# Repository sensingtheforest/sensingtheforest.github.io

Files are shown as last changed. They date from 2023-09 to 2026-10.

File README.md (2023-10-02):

# Sensing the Forest - project website

This project website is using [11TA](https://github.com/11ta/11ta-template/) - 11ty, TailwindCSS, & Alpine.js Template.

## Run it manually in localhost

- Clone the repository locally
- Run `npm install` to install dependencies
- `npm run dev` to work locally

## Run it in production

- `npm run build` to work in production

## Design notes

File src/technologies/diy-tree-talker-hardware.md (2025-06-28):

---
title: DIY Tree Talker | Hardware
date: 2025-06-27T07:30:00.000Z
excerpt: The hardware component of the DIY Tree Talker.
layout: post
draft:
seo:
  title: DIY Tree Talker | Hardware
  description: The hardware component of the DIY Tree Talker.
  image: technologies/diy-tree-talker-hardware-northern-research-station.jpg
images: # relative to /src/assets/images/
  #feature: exhibition/Peter-Batchelor-Dendrophone-overview_by_Shuoyang_Zheng.jpg
  thumb: technologies/diy-tree-talker-hardware-northern-research-station.jpg
  align: # object-center (default) - other options at https://tailwindcss.com/docs/object-position
  height: h-auto # optional. Default = h-48 md:h-1/3
hero: graphic # options: carousel, graphic, video, split (text & image)
heroSettings:
  height:
    mobile: h-1/1 # options = h-1/1 (default = full screen), h-1/2, h-1/3, h-3/4, h-9/10, h-48 (12rem, 192px), h-56 (14rem, 224px), h-64 (16rem, 256px)
    desktop: # leave blank to inherit "mobile" height (default = full screen)
  bg:
    color: bg-green-900 # default bg-black
    image: technologies/diy-tree-talker-hardware-northern-research-station.jpg # relative to /assets/images/
    imagePosition: # options = bg-center (default), bg-left, bg-right
    video: # pixabay-john-macdougall.mp4 # local relative /assets/video/, or full https://... if remote?
    opacityMobile: opacity-50 # options opacity-n, 5, 10, 15, 20, 25, 50, 75, 100 (default)
    opacityDesktop: opacity-75 # Leave blank to inherit opacityMobile, use same options as opacityMobile
  headingText: DIY Tree Talker | Hardware
  headingTextColor: # default = text-white (can use any TailwindCSS text-[color]-[xxx])
  headingTextCase: # default = as typed - options: uppercase, lowercase, capitalize
  subheadingText: #
    #Let the Forest Speak using the Internet of Things, Acoustic Ecology and Creative AI<br /><span style="color:grey">AHRC-funded project (2023-25) : AH/X011585/1</span>
  subheadingTextColor: # Leave empty to inherit headingTextColor or default (text-white) or use any text-[color]-[xxx]
  buttonText: # Contact Us... # no button generated if left blank
  buttonURL: # /contact/ # full url required. Example: https://thisdomain.com/somepage/
  buttonTextColor: # leave blank to inherit from /src/_data/colors.buttonCustom or buttonDefault
  buttonBgColor: # leave blank to inherit from /src/_data/colors.buttonCustom.bg or buttonDefault.bg
  buttonBgHover: # leave blank to inherit from /src/_data/colors.buttonCustom.bgHover or buttonDefault.bgHover
  buttonBorder: # leave blank to inherit from /src/_data/colors.buttonCustom.border or buttonDefault.border
  
tags:
  - technologies

---

### Authors: Mahmoud B. Elmokadem, Krishna Nama Manjunatha, Georgios Xenakis, Anna Xambó

*A Real-World Deployment of the Streaming Unit. 
:camera: *Photo by Mahmoud B. Elmokadem.**

The system integrates a suite of sensors—including a capacitive soil moisture sensor, a combined temperature and humidity sensor, and a bespoke dendrometer, connected to a Raspberry Pi Zero 2W for data acquisition and processing.

A custom tree-talker prototype is being developed, using a participatory design approach. The device comprises a soil moisture sensor, a combined temperature and humidity sensor, and a bespoke dendrometer, connected to a Raspberry Pi Zero 2W single-board computer for data acquisition. You can read about our dendrometer in our tutorial [Design of Cost Effective IOT Dendrometer Sensor for Environmental Monitoring](/2025/05/05/design-of-cost-effective-iot-dendrometer-sensor-for-environmental-monitoring/).

<div class="flex justify-center items-center">
<figure>
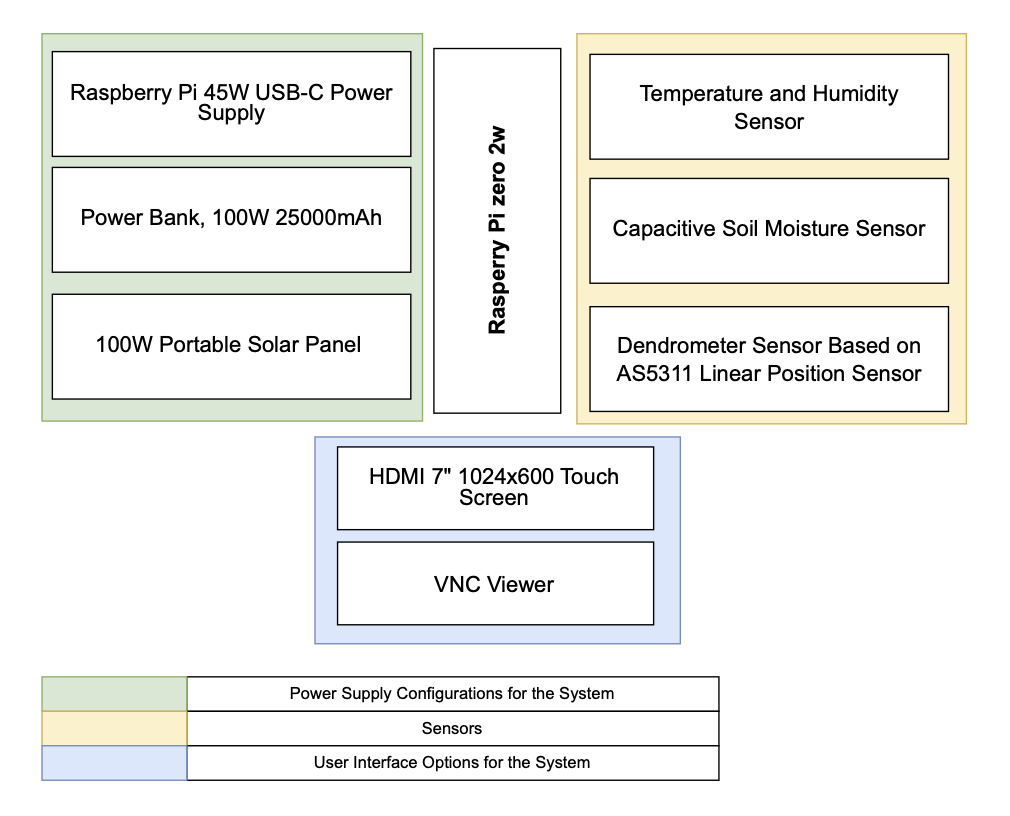
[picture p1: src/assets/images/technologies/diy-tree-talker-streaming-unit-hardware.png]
Hardware Configuration Overview of the Sensing Unit.

<figcaption>Hardware Configuration Overview of the Sensing Unit.</figcaption>
</figure>
</div>

Traditional dendrometer systems often come with high costs and complex installation requirements, limiting their accessibility for small-scale researchers; thus, a custom, cost-effective dendrometer was iteratively designed, based on Clonch and colleagues’ open-source magnetic carbon fibre dendrometer [1]. To further reduce costs, we replaced the carbon fibre frame with 3D-printed components made from high-density PLA, and captured data using the Raspberry Pi, reducing the overall cost by 50%, without compromising core functionality.
 
The main chassis of the dendrometer sensor is secured to the tree/plant using a strap, ensuring stable attachment without causing any damage to the bark or applying external stress. A movable component, referred to as the T-shaped magnet mount, is connected to the chassis via an extension spring and is positioned to slide forward and backwards in response to the tree/stem’s natural expansion or contraction. These micro-movements—often in the micrometer range—are detected by the AS5311 magnetic linear encoder, which precisely tracks the relative position of the magnet. The sensor transmits data to the Raspberry Pi Zero 2W via a PWM (Pulse Width Modulation) signal, which is then processed and converted into readable measurements that reflect changes in stem diameter over time. The sensor is integrated into a larger sensing unit that also includes additional climatic sensors to monitor environmental parameters such as temperature, humidity, and soil moisture, alongside the tree’s natural expansion or contraction. All collected data is streamed to a central server for real-time monitoring and analysis.

<div class="flex justify-center items-center">
<figure>
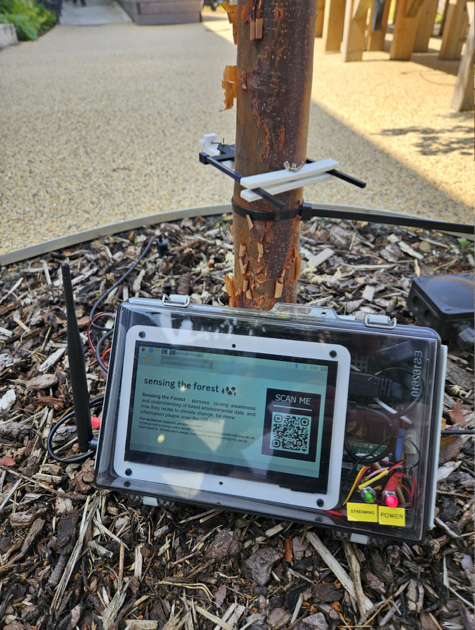
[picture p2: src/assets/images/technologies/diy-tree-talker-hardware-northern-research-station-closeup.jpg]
Closeup of a real-world deployment of the streaming unit.

<figcaption>Closeup of a real-world deployment of the streaming unit. Photo by Mahmoud B. Elmokadem.</figcaption>
</figure>
</div>

:fire: We are currently running a participatory design user study. We will share the hardware code soon on our [GitHub project webpage](https://github.com/orgs/sensingtheforest/repositories).

## List of References

[1] Clonch, C., Huynh, M., Goto, B., Levin, A., Selker, J. and Udell, C., 2021. [High precision zero-friction magnetic dendrometer](https://www.sciencedirect.com/science/article/pii/S246806722100078X). HardwareX, 10, p.e00248.

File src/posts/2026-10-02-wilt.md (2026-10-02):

---
title: WILT – Using Solar-Powered Kinetic Art to Communicate Climate Change
date: 2026-10-01T10:00:00.000Z
excerpt: WILT is a solar-powered kinetic art installation in which five servo-driven paper flowers breathe freely or struggle depending on live air quality data fetched in real time from cities around the world. 
author: dharma-rumpal
draft:
seo:
  title:
  description:
  image: 2026/10/WILT_Dharma_Rumpal.jpg
images: # relative to /src/assets/images/
  feature: 2026/10/WILT_Dharma_Rumpal.jpg
  thumb: 2026/10/WILT_Dharma_Rumpal.jpg
  align: # object-center (default) - other options at https://tailwindcss.com/docs/object-position
  height: h-auto # optional. Default = h-48 md:h-1/3
tags:
  - climate-change
  - hardware
  - kinetic-art
  - software
  - solar
  - solar-powered  
  - theses

---

<br />

## Introduction

Climate change is one of the most pressing issues of our time, yet public engagement remains critically inadequate. Traditional communication methods such as: statistics, scientific reports, and news headlines, frequently fail to create the emotional resonance needed to inspire action. For my final year project at Queen Mary University of London, I set out to explore whether interactive art powered by renewable energy could bridge this gap in a way that data alone never could.

The result was Wilt: a solar-powered kinetic art installation in which five servo-driven paper flowers breathe freely or struggle depending on live air quality data fetched in real time from cities around the world. The piece cycles through ten globally selected cities every 45 seconds, from Reykjavik in Iceland, one of the cleanest cities on earth, to Delhi and Beijing at the other extreme. As the data changes, so does the movement of the flowers. Good air quality produces full, open blooms moving freely. Poor air quality produces slow, laboured, restricted movement. 

<div class="flex justify-center items-center">
<figure>
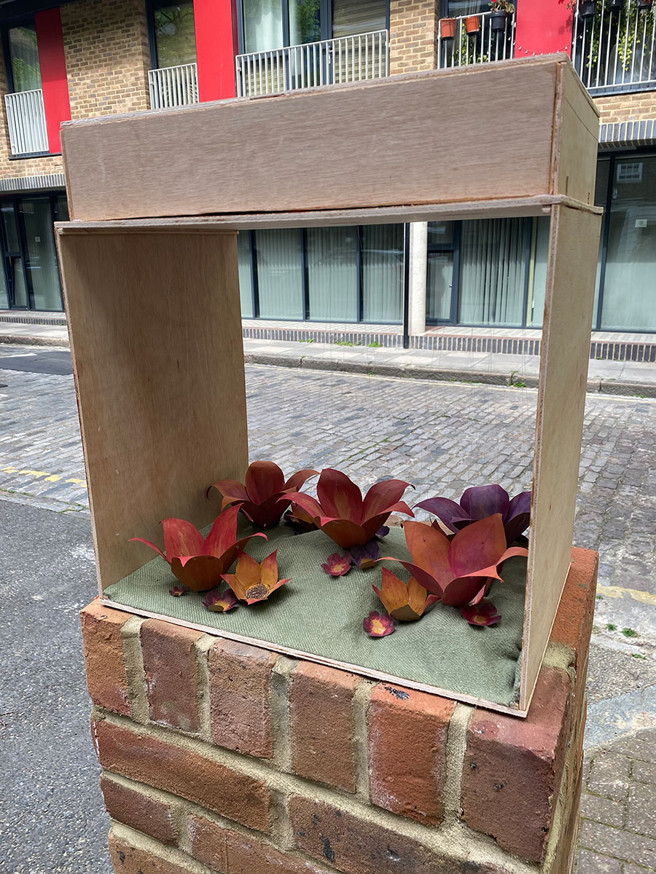
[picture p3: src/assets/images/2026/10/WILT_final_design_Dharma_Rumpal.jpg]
Final design.

<figcaption>Final design.</figcaption>
</figure>
</div>

## Development 

The technical system behind the installation brings together several layers of software and hardware working as one. An Arduino Uno microcontroller manages five SG90 servo motors through a synchronised breathing function, with movement speed and range calibrated precisely to each air quality state. A Python control script handles all the intelligence, making live API calls to the [OpenWeatherMap Air Pollution API](https://openweathermap.org/api/air-pollution), converting the data, and transmitting commands to the Arduino over USB serial. The whole system runs on renewable energy: a 5W solar panel charges an 18650 lithium-ion battery through a TP4056 charging module, stepped up to stable 5V by an XL6009 boost converter. The solar infrastructure was deliberately left visible as the power system is part of the message, not infrastructure to be hidden.

<div class="flex justify-center items-center">
<figure>
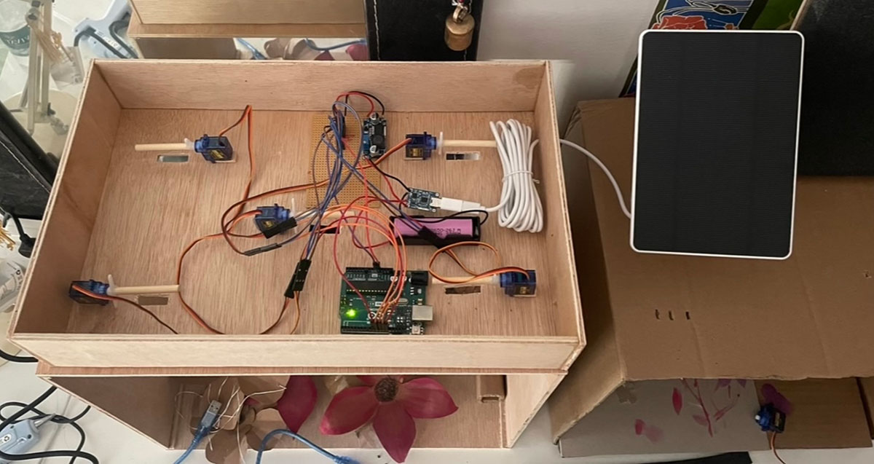
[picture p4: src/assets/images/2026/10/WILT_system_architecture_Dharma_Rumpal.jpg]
System architecture.

<figcaption>System architecture.</figcaption>
</figure>
</div>

A companion website extended the installation's reach beyond the physical display, featuring a live city monitor kept in sync with the flowers, an interactive global air quality map, and educational pages on AQI and solar power.

## Evaluation 

What distinguishes Wilt from much of the climate art that preceded it is that it was systematically evaluated. The installation was exhibited at Queen Mary University of London, where participants completed paired pre and post surveys and took part in semi-structured interviews. The findings were significant. Climate concern rose from 3.84 to 4.48 out of 5. Motivation to act increased from 3.56 to 4.35. Most strikingly, the proportion of participants who considered interactive art installations an effective method of climate communication rose from 20% before the exhibition to 96% after it. The dominant emotional responses were curiosity, hope, and inspiration, not fear or helplessness.

## Conclusion 

Wilt contributes something that has been largely absent from the field of climate communication: connection. And now a  methodological template now exists for how data-responsive kinetic art, renewable energy infrastructure, and rigorous evaluation can work together. One that future artists, researchers, and climate communicators can take, replicate, and build upon. 

## Acknowledgements

I would like to express my sincere gratitude to my supervisor Dr Anna Xambó Sedó, for her unwavering guidance, support, and feedback throughout this project. I would also like to thank Kok Ho Huen, the electronics lab manager at Queen Mary University of London, and David Wilkinson, the electronic lab technician, for their helpful knowledge and advice, and for providing access to the resources that made the physical build possible. Finally, I would like to thank my brother, Cosmo Rumpal, for composing the original music tracks that brought the installation to life. His contribution added a dominion to the project I could not have achieved alone.

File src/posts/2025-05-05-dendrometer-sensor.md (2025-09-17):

---
title: Design of Cost Effective IOT Dendrometer Sensor for Environmental Monitoring 
date: 2025-05-05T10:00:00.000Z
excerpt: In this tutorial, we introduce the design of a customised dendrometer sensor for our DIY tree talker.
author: mahmoud-elmokadem
author2: krishna-nama-manjunatha
draft: 
seo:
  title:
  description:
  image: 2025/05/DIY-tree-talker.jpg
images: # relative to /src/assets/images/
  feature: 2025/05/DIY-tree-talker.jpg
  thumb: 2025/05/DIY-tree-talker.jpg
  align: # object-center (default) - other options at https://tailwindcss.com/docs/object-position
  height: h-auto # optional. Default = h-48 md:h-1/3
tags:
  - dendrometer
  - development
  - diy-tree-talker
  - do-it-yourself
  - raspberry-pi
  - tutorials
 
---

## Introduction

Monitoring tree growth is essential for understanding forest health, ecosystem dynamics, and climate change impacts. At the heart of this process is the dendrometer sensor—an instrument designed to measure changes in a tree’s diameter over time. This helps to understand seasonal, and annual growth patterns in response to environmental conditions. As this is linked to and can be correlated with the tree diameter fluctuations with temperature, rainfall, humidity, and soil moisture and identify the stress events like droughts, heatwaves, or cold spells. Growth data of the tree can be used to estimate biomass accumulation, indicate root damage or poor soil conditions, and growth with respect to fertilizers, irrigation regimes and climate.  However, traditional dendrometer systems often come with high costs and complex installation requirements, limiting their accessibility for small-scale researchers, farmers, and institutions in low-resource settings. As environmental monitoring becomes more critical globally, there's a growing demand for affordable, reliable, and scalable solutions. A cost-effective dendrometer sensor can democratise access to valuable data, enabling broader participation in ecological research and resource management. By reducing financial barriers, we not only make long-term monitoring feasible but also support sustainable practices in both forestry and agriculture.

## Overview of Different Types of Dendrometer Sensors

There are various types of dendrometers currently used by researchers and scientists to measure changes in the diameter of trees, plants, or even fruits. While the designs may differ, they all share a similar sensing mechanism aimed at achieving the same objective: tracking dimensional changes over time to study growth patterns, water transport, and environmental stress responses. The most common types include point dendrometers, band dendrometers, and manual dendrometers as shown in Figure 1. 

<div class="flex justify-center items-center">
<figure>
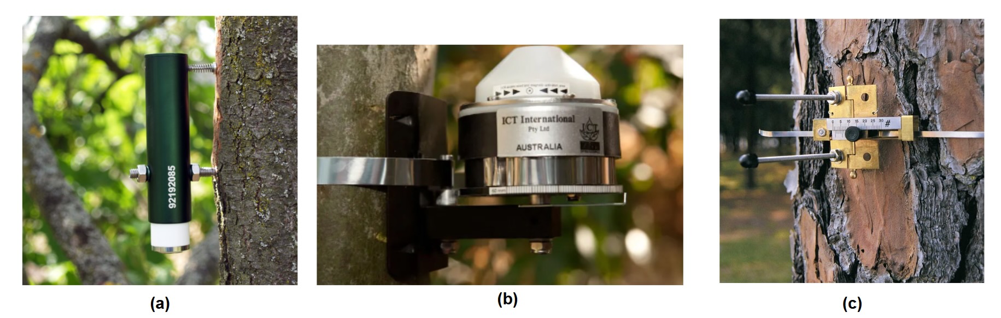
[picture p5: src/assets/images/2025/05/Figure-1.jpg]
Figure 1. Comparison with different types of commercially available dendrometers (a) Point Dendrometer [1] (b) Band Dendrometers [2] (c) Manual Band Dendrometers [3].

<figcaption>Figure 1. Comparison with different types of commercially available dendrometers (a) Point Dendrometer [1] (b) Band Dendrometers [2] (c) Manual Band Dendrometers [3].</figcaption>
</figure>
</div>

Point dendrometers use a single contact point against the bark to detect radial changes. Band dendrometers wrap around the stem or trunk and measure circumference changes, making them ideal for long-term monitoring. Manual band dendrometers uses a tape measurement warp around the stem or trunk. Despite their effectiveness, many of these instruments are expensive, complex, or power-intensive—limiting their use in remote, large-scale, or low-budget projects. This highlights the growing need for a simplified, cost-effective dendrometer that maintains accuracy while being affordable, easy to deploy, and suitable for long-term environmental monitoring.

## Designing a Cost-Effective Dendrometer Sensor

The proposed cost-effective dendrometer sensor design is heavily based on an open-source magnetic dendrometer as described in this research paper [4]. In that study, the researchers developed a dendrometer using a carbon fibre frame (as shown in Figure 2) and utilised the AS5311 magnetic sensor to capture the change in diameter of the tree/branch, data was processed using an Arduino-based microcontroller. Reported total cost was approximately $260 per unit.

<div class="flex justify-center items-center">
<figure>
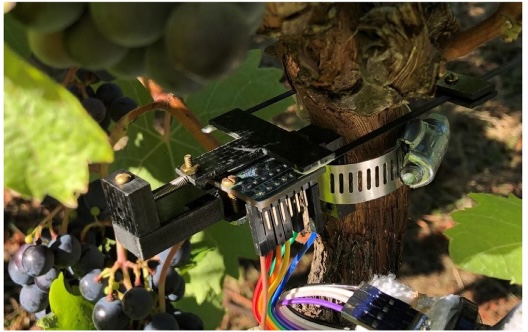
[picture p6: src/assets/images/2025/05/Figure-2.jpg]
Figure 2. Carbon fibre based dendrometer sensor.

<figcaption>Figure 2. Carbon fibre based dendrometer sensor.</figcaption>
</figure>
</div>

Building on their approach with a focus on cost reduction, we made two key modifications: replacing the carbon fibre frame with 3D-printed components made from high-density PLA and using a industrial accepted Raspberry Pi Zero 2W single-board computer for data acquisition. These changes enabled us to reduce the overall cost by 50%, making the solution significantly more affordable without compromising core functionality.

## Dendrometer Sensor Design

Details of our modified version are presented below. Figure 3 illustrates the final design of the cost-effective dendrometer sensor, representing the 3D CAD model of the sensor. Final prototype was achieved after several iterations, with multiple versions developed and tested for each component throughout the design process. These developmental stages are shown in Figures 4, 5, and 6. Each version contributed valuable insights, helping us refine the mechanical structure, sensor placement, and integration with the Raspberry Pi. By systematically evaluating and improving individual parts, we achieved a compact, robust, and low-cost solution suitable for long-term outdoor use.

<div class="flex justify-center items-center">
<figure>
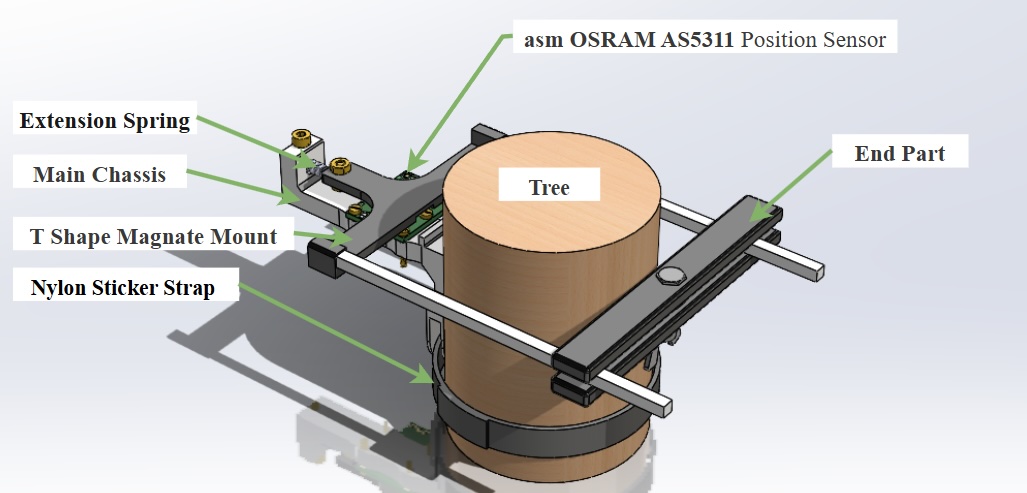
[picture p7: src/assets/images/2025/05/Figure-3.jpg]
Figure 3. Various parts of the dendrometer that is designed in this work.

<figcaption>Figure 3. Various parts of the dendrometer that is designed in this work.</figcaption>
</figure>
</div>

<div class="flex justify-center items-center">
<figure>
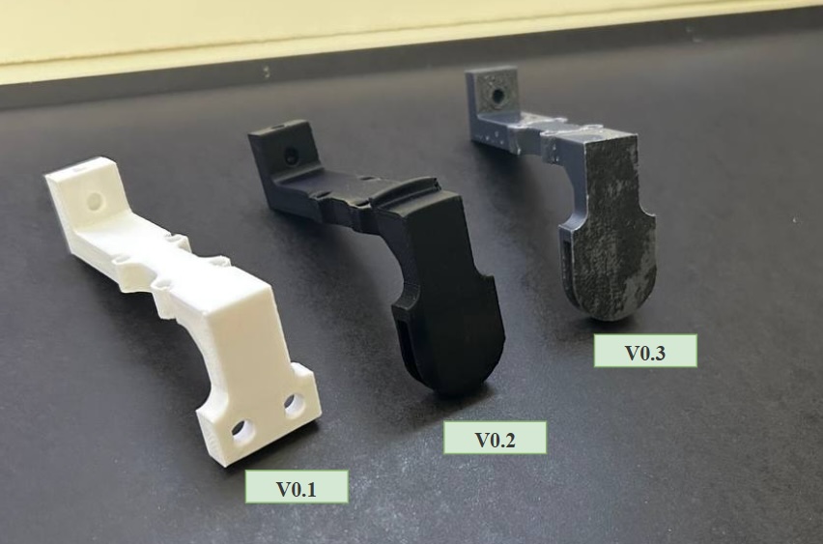
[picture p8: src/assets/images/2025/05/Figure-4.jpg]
Figure 4. Different version for the main chassis that was used and modified to achieved more reliable and repeatable measurements

<figcaption>Figure 4. Different version for the main chassis that was used and modified to achieved more reliable and repeatable measurements.</figcaption>
</figure>
</div>

<div class="flex justify-center items-center">
<figure>
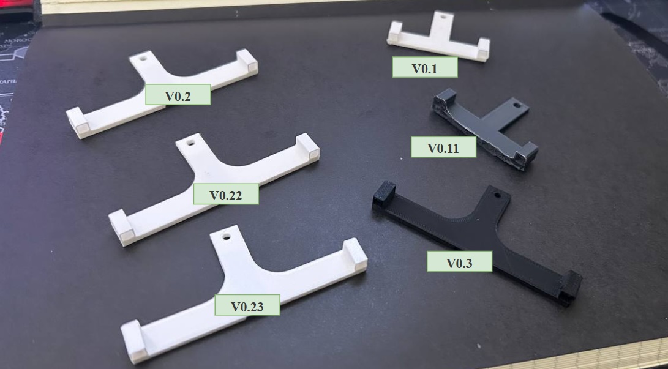
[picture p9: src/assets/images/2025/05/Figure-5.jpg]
Figure 5. Different versions designed for the T shape mount to accommodate the magnet sensor and the magnet.

<figcaption>Figure 5. Different versions designed for the T shape mount to accommodate the magnet sensor and the magnet.</figcaption>
</figure>
</div>

<div class="flex justify-center items-center">
<figure>
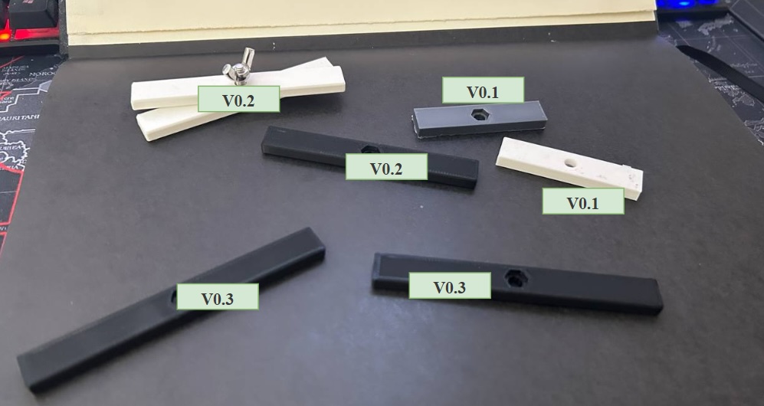
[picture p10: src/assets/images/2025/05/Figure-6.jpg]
Figure 6. Carbon fibre based dendrometer sensor.

<figcaption>Figure 6. Carbon fibre based dendrometer sensor.</figcaption>
</figure>
</div>

## Working Principle of the Dendrometer Sensor

<div class="flex justify-center items-center">
<figure>
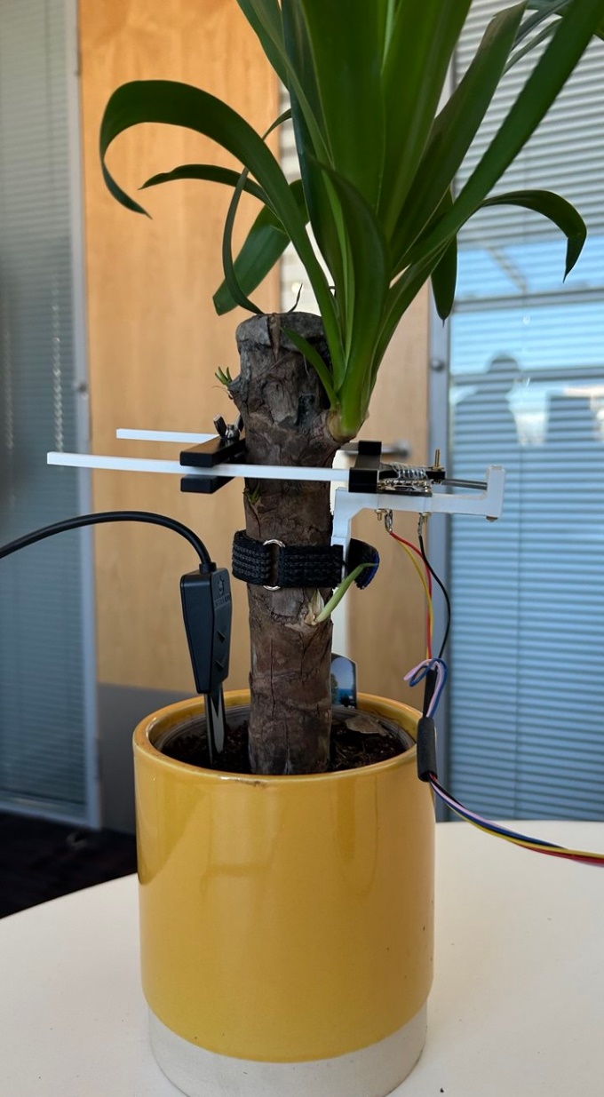
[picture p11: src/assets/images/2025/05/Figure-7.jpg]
Figure 7. Dendrometer sensor connected to Yucca Plant to carry out measurements and remotely stream the data of key parameters.

<figcaption>Figure 7. Dendrometer sensor connected to Yucca Plant to carry out measurements and remotely stream the data of key parameters.</figcaption>
</figure>
</div>

The main chassis of the dendrometer sensor is secured to the tree/plant using a strap, ensuring stable attachment without causing any damage to the bark or applying external stress. A movable component, referred to as the T-shaped magnet mount, is connected to the chassis via an extension spring and is positioned to slide forward and backward in response to the tree/stem’s natural expansion or contraction. These micro-movements—often in the micrometer range—are detected by the AS5311 magnetic linear encoder, which precisely tracks the relative position of the magnet. The sensor transmits data to the Raspberry Pi Zero 2W via a PWM (Pulse Width Modulation) signal, which is then processed and converted into readable measurements that reflect changes in stem diameter over time. The sensor is integrated into a larger sensing unit that also includes additional sensors to monitor environmental parameters such as temperature, humidity, and soil moisture—alongside the tree’s natural expansion or contraction. All collected data is streamed to a central server for real-time monitoring and analysis. The complete unit is shown in Figure 8, while a sample of the recorded sensing data is presented in Figure 9. 

<div class="flex justify-center items-center">
<figure>
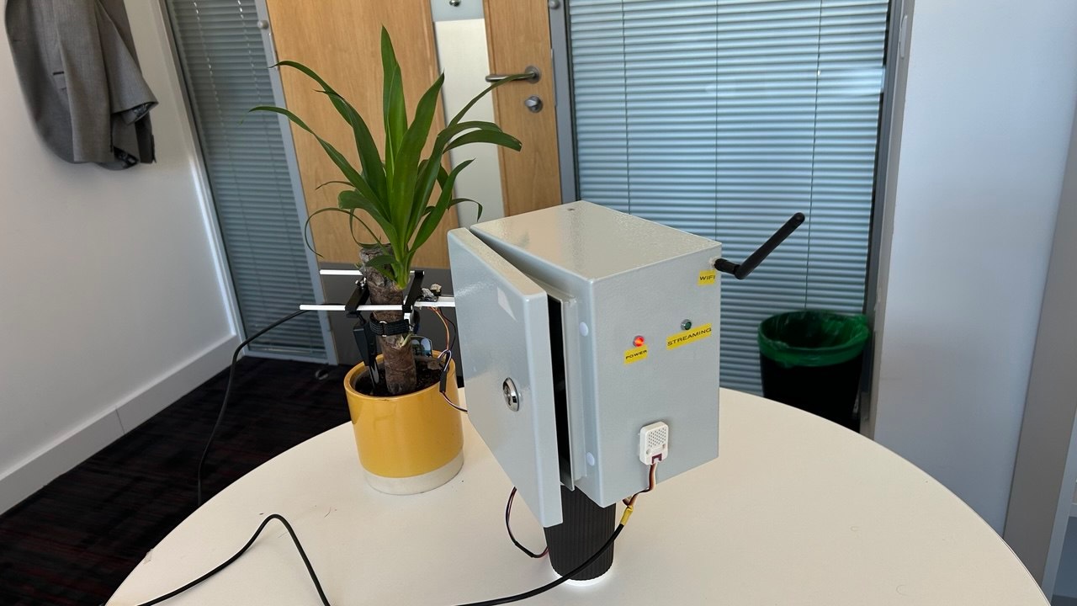
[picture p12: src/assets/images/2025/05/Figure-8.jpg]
Figure 8. Sensing the Forest DIY IOT Sensing Unit that measures and streams data such as temperature, humidity, soil moisture, and tree diameter.

<figcaption>Figure 8. Sensing the Forest DIY IOT Sensing Unit that measures and streams data such as temperature, humidity, soil moisture, and tree diameter.</figcaption>
</figure>
</div>

<div class="flex justify-center items-center">
<figure>
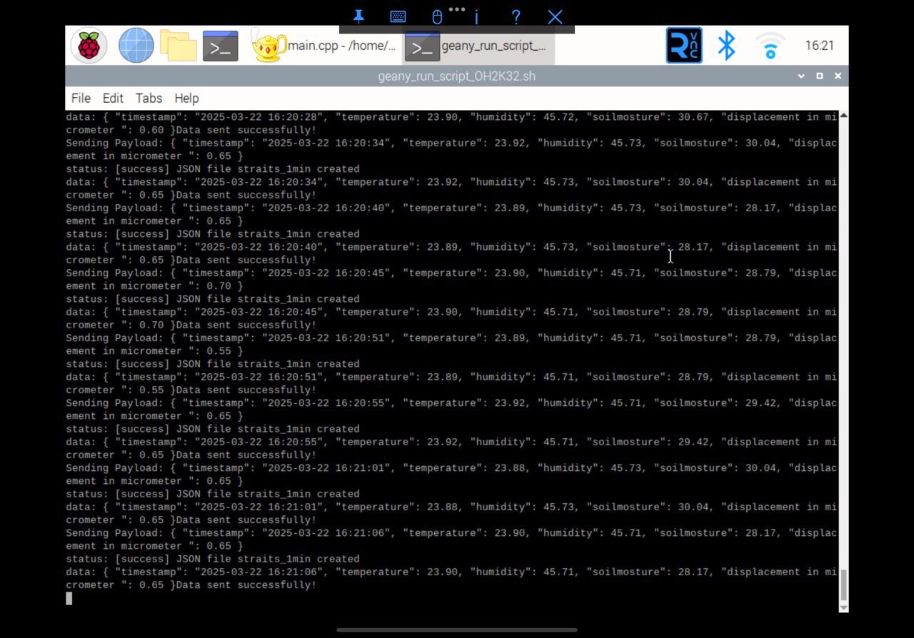
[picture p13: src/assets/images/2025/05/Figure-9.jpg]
Figure 9. Streaming data from the Raspberry Pi Zero remotely with all the key parameters required to understand the health of a tree.

<figcaption>Figure 9. Streaming data from the Raspberry Pi Zero remotely with all the key parameters required to understand the health of a tree.</figcaption>
</figure>
</div>

## List of References

[1] https://tomst.com/web/events/point-dendrometer/ 
[2] https://ictinternational.com/product/band-dendrometers/ 
[3] https://jeetekno.com/product/series-5-manual-band-dendrometers/ 
[4] Clonch, C., Huynh, M., Goto, B., Levin, A., Selker, J. and Udell, C., 2021. [High precision zero-friction magnetic dendrometer](https://www.sciencedirect.com/science/article/pii/S246806722100078X). HardwareX, 10, p.e00248.

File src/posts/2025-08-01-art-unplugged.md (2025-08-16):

---
title: Art, Unplugged - In the search of a sustainable off-grid power solution for immersive art installations
date: 2025-08-01T07:00:00.000Z
permalink: /2025/08/01/art-unplugged/
excerpt: The inspiration for my final year project came from the Sensing the Forest project, which focuses on collaborative and interdisciplinary approaches to studying the relationship between forests and climate change. 
author: aleksander-skutnik
draft: false
seo:
  title:
  description:
  image: 2025/08/2024-12-06-Peter_Batchelor_and_Alex_Skutnik_closeup.jpg #
images: # relative to /src/assets/images/
  feature: 2025/08/2024-12-06-Peter_Batchelor_and_Alex_Skutnik_closeup.jpg #
  thumb: 2025/08/2024-12-06-Peter_Batchelor_and_Alex_Skutnik_closeup.jpg #
  align: # object-center (default) - other options at https://tailwindcss.com/docs/object-position
  height: h-auto # optional. Default = h-48 md:h-1/3
tags:
  - artistic-solar-powered-solutions
  - interviews
  - theses
  - machine-learning
  - research
  - software
  - solar-panels
  - technologies

---

*From left-right, Aleksander Skutnik and Peter Batchelor.*

## Introduction

The inspiration for this project came from the Sensing the Forest project, which focuses on collaborative and interdisciplinary approaches to studying the relationship between forests and climate change. As I personally find this topic very important in terms of being a global issue, for my final year project I have decided to develop a project in that domain under pivotal supervision of Dr Anna Xambó Sedó.

## Aim

For years now, it has been very well documented how excessive electrical energy production highly contributes to greenhouse gas emissions worldwide. With the very rapidly increasing interest and demand for immersive and digital art installations, we can see how energy usage proportionally rises. In order to counter this, this project aims to answer the question: **How can we devise a power solution to achieve selfsustainability of art installations, and how can we apply this knowledge in the art industry?**

## Field Study

An initial step in carrying out my project was a site visit to the Alice Holt Forest, specifically the *Dendrophone* installation by Dr Peter Batchelor and the *Streamers* by Dr Luigi Marino. I had the pleasure to visit onsite in the company of my project supervisor Dr Anna Xambó Sedó where we also met Dr Peter Batchelor. Together, we were able to see hands-on how the installations operate and their technical aspects. Dr Peter Batchelor very kindly answered all of my questions regarding his work, and I was also then able to interview him on site in an office space we booked for the day, courtesy of Forestry England. The interview has been published on the Sensing the Forest website. This visit has helped me study the theoretical background for my project and see how my topic could apply to existing real life installations. I believe that was an essential step to this project in order to ground my research and findings in a real world context.

## Interviews

In order to build a theoretical framework backing up my proposed solution, I have decided to carry out a series of interviews with artists who have experience with integrating solar power in their work. I have personally reached out via email to a number of artists that have relevant experience in this field and arranged a range of interviewssome of them being in person, online or over email. [Dr Peter Batchelor](/2025/02/08/an-interview-with-peter-batchelor/), **Dr Luigi Marino**, [Dr Chris Meigh-Andrews](/2025/03/14/an-interview-with-chris-meigh-andrews/), [Sarah Hall](/2025/03/10/an-interview-with-sarah-hall/), **Elizabeth Monoian**, **Robert Ferry**, **Alex Nathanson** and **Shala Akintunde** have all very kindly agreed to take part in the study. The questions asked about the artists’ background in art and solar power, the technical aspects behind the operation of their installations, benefits and challenges the artists have faced while implementing solar power and any visions/ideas/values they associate with integrating solar power as a green, renewable energy source for their installations.

Insights from these interviews gained in the process of thematic analysis helped me shape the theoretical framework and identify system requirements essential for the proposed solution I will discuss later on. I believe reaching out to artists was crucial for this project, as they will be the end users of the solution - thus, their insights and experiences are pivotal in the construction of said solution.

## Proposed solution

This part of the project introduces an initial prototype of a **solar forecasting and battery simulation tool**:

* **Data source**: `PVGIS` solar irradiance API.
* **ML forecasting**: `RandomForestRegressor` predicts energy inflows.
* **Battery model**: Simulates charge/discharge cycles across multiple days.
* **User interface**: Built in `Streamlit` for users to input location, system specifications, time of year and day and see visualised output.

The tool calculates daily energy yield and battery status, letting users explore seasonal variability and system resilience. This is especially beneficial while planning installations to see if their operation basing on solar power is feasible and executable. The working initial prototype with instructions on how to run can be found [here](https://github.com/askutnik/artunplugged).

The screenshots below present the interactive user dashboard of my solution. The user inputs all geographical data for the conditions they want to forecast, e. g. location, tilt angle and azimuth of the PV panel. Then, the program fetches PVGIS database data using and API call and presents two graphs. The first one shows actual solar irradiance data across five years for the specified location which is taken from the PVGIS database.

<div class="flex justify-center items-center">
<figure>
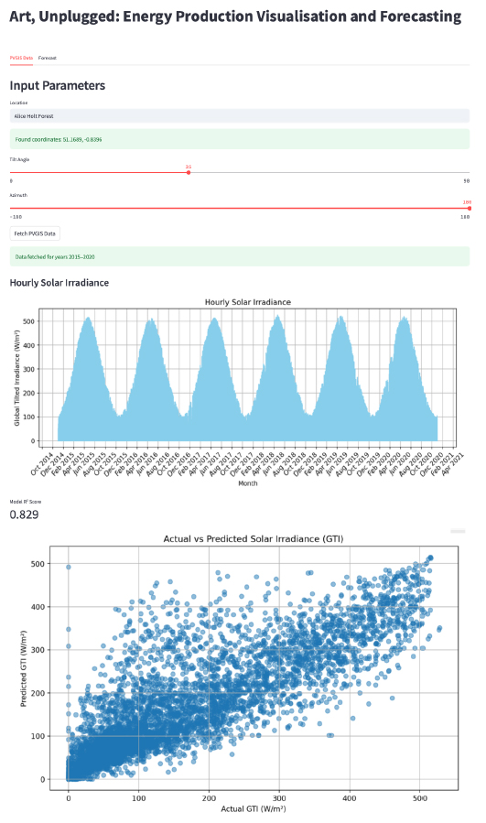
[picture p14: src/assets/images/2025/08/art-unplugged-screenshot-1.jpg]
Screenshot of energy production visualisation and forecasting.

<figcaption>Screenshot 1 of Art Unplugged: Energy production visualisation and forecasting.</figcaption>
</figure>
</div>

This shows the user how solar irradiance has been changing over time for the specified location and allows them to understand which months bring the highest levels of solar irradiance. Then, a machine learning model for forecasting Global Tilted Irradiance (GTI) is trained on the fetched data and then compared in a scatter plot graph to actual solar irradiance values. The model’s R2 score is also presented. This is for the purpose of demonstrating how accurate the model actually is in predicting GTI values. 

On the second tab is dedicated for solar irradiance forecasting and battery charge/discharge cycle simulation. The user inputs all required details, including the month of the year they want to forecast for, how many days the forecast should cover, battery capacity in Ah of their installation, system voltage of their installation, the power rating of their PV panel setup and the total load power of the installation. 

<div class="flex justify-center items-center">
<figure>
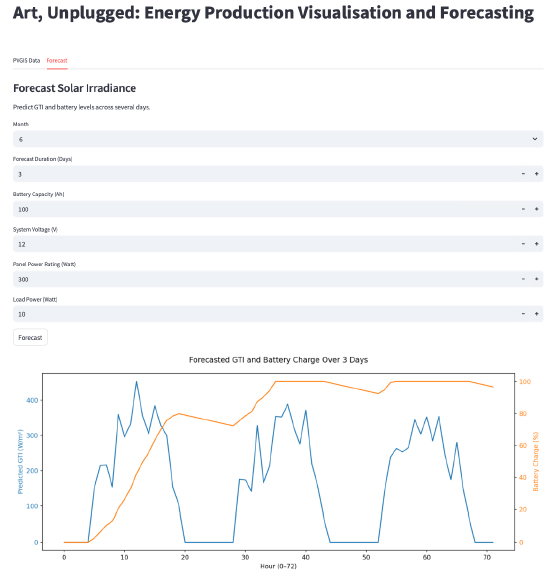
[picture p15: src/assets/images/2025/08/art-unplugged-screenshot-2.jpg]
Screenshot of energy production visualisation and forecasting.

<figcaption>Screenshot 2 of Art Unplugged: Energy production visualisation and forecasting.</figcaption>
</figure>
</div>

With those specifications, the previously trained model predicts the solar irradiance values across the number of days selected by the user. Additionally, the battery charge and discharge cycles are presented on a continuous line basing on the solar irradiance availability across the different hours of the day. I believe that this tool can be really helpful for artists who are in the process of planning and designing their installation in order to determine how to make their power solution viable and functional under specified by them conditions.

## Conclusion

This project was a great learning experience for me. What I loved about it most is being able to work with so many inspiring and knowledgeable individuals without whom I would not be able to achieve the goals of my project. I am really happy with the fact that I was able to study and explore a global issue in depth while at the same time applying it in an academic context, as well as exploring how the scientific and artistic domain converge.

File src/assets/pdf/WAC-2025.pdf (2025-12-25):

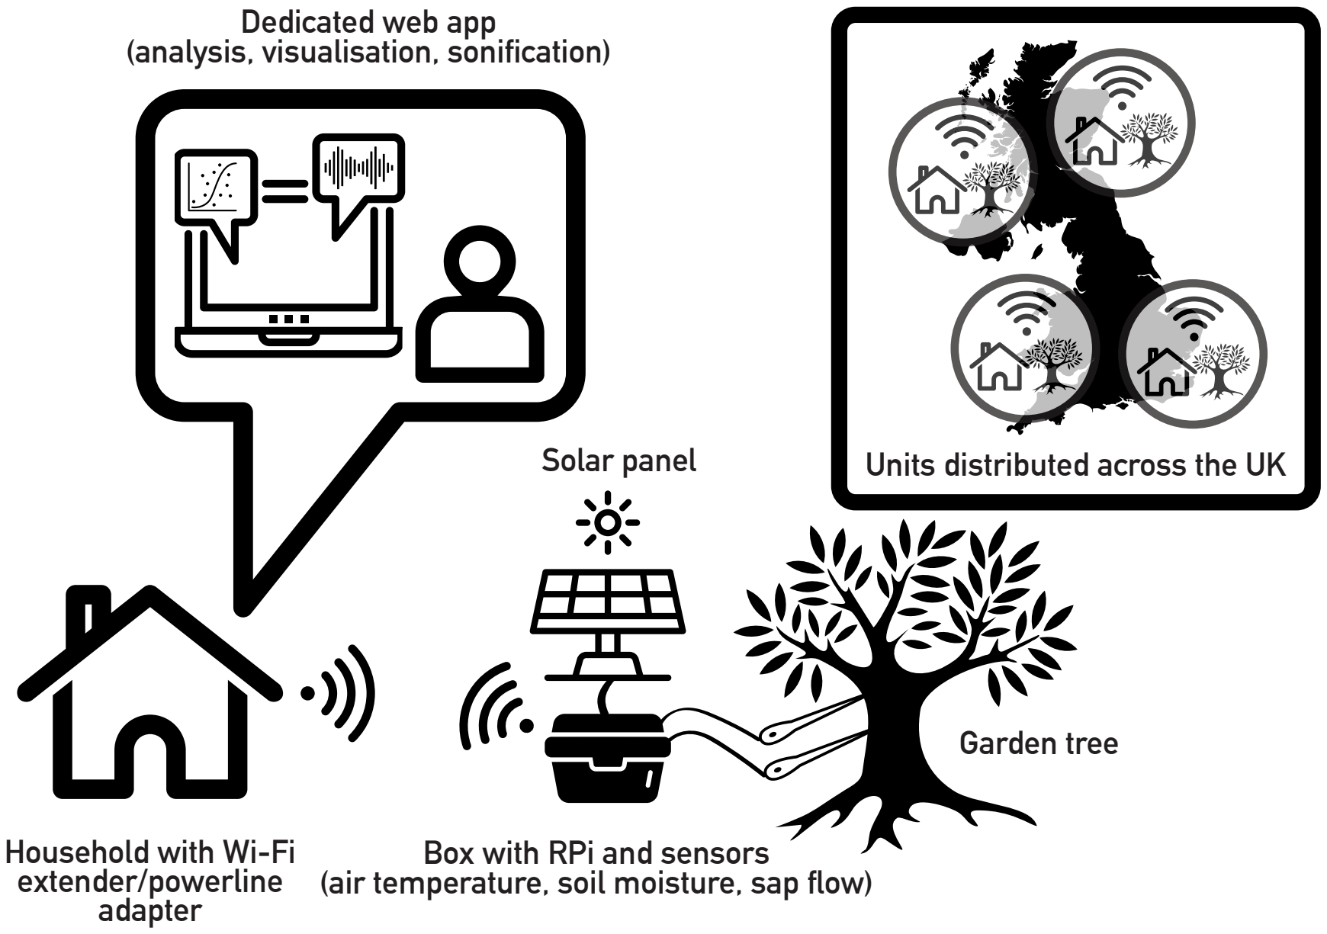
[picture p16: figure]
Box with RPi and sensors; Household with Wi-Fi extender/powerline adapter; Units distributed across the UK; Garden tree; Solar panel
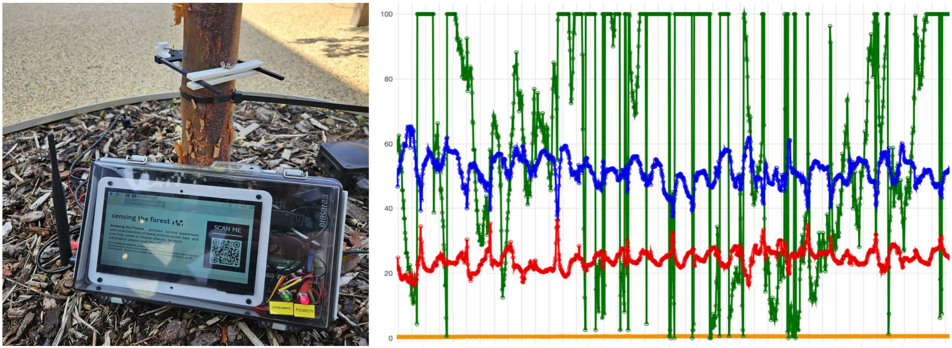
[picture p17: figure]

### Web Audio Conference (WAC ’25), 19-21 November 2025, Paris, France

This research receives funding from the UKRI Arts and Humanities Research Council (AH/X011585/2)

School of Electronic Engineering and Computer Science

# Sonification Mappings for Sensing Tree Stress: A DIY Approach

Centre for Digital Music, Queen Mary University of London
Tug F. O’Flaherty, Mahmoud B. Elmokadem, Xinyue Xu, Krishna Nama Manjunatha, Gerard Roma, Georgios Xenakis, Anna Xambó Sedó
{t.f.oflaherty, x.xu}@se24.qmul.ac.uk, {mahmoud.elmokadem, krishna.namamanjunatha}@dmu.ac.uk, gerard.roma@uwl.ac.uk, georgios.xenakis@forestresearch.gov.uk, a.xambosedo@qmul.ac.uk

## Research Question

What are suitable mappings (data-to-sound associations) from weather data to sound data that can raise awareness about climate change?

(air temperature, soil moisture, sap flow)

Dedicated web app (analysis, visualisation, sonification)

Project vision: our low-cost DIY tree-talker prototype’s hardware and software workflow.

A real-world deployment of the hardware unit (left) and interactive software (right)

## Sensing the Forest

Sensing the Forest (StF) aims to raise awareness among forest visitors, artists, scientists, and the general public about the connection between forests and climate change.

Our vision is to emphasise listening as a method to engage with the forest ecosystem.

## System Software

## Basic Mappings

Two simple one-to-one mapping sonifications are proposed, mapping sensor data to separate drone sounds or frequency modulation (FM) synthesiser parameters, accompanied by a line graph visualisation.

- Drone Mapping: tone frequency changes with respect to corresponding value using natural mapping (high values -> high tones).
- FM Synthesis Parameter Mapping: carrier frequency (temperature), modulator frequency (humidity), modulation index (dendrometer), and carrier gain (soil moisture) calculated using suitably rescaled values with natural mapping.

## Complex Mappings

Users may create custom sonifications from the data, or sonify data inferred from the sensor readings, optionally accompanied by graph or animated visualisations.

- Custom Sonification: users design their own sonifications, selecting instruments for each data variable, tempo, rhythm and note duration preferences, and a starting pitch or scale for the tool to use to map the sensor data. Chords, drums, instrument track volumes, spatial location, and audio effects may be selected using the dropdown list-based tool, with the final piece able to be played back or saved.
- Inference: Performing calculations using the sensor reading values provides further insights into tree stress, including daily tree shrinkage and expansion, a tree's response to climate, its mean growth, and tree canopy air dryness. These inferred values may be sonified using a drone soundscape, FM synthesis parameter, or custom sonification mapping method.

## System Hardware

Backend:
A custom RESTful API shares regular JSON data via endpoints corresponding to URLs. Sensor data is received from the tree-talker hardware unit, and saved separately on the web server.

Frontend:
Directly accessible REST endpoints are available to:
•View unit’s latest record.
•View unit’s historical records.
•Interact with visualisations and sonification of unit’s data.

A custom tree talker prototype offers affordability and ease of use for monitoring a tree and its climate. Sensors connected to a Raspberry Pi, for processing, include:

- Custom low-cost 3D-printed non-invasive magnet-based dendrometer (to measure tree trunk diameter changes).
- Soil moisture and temperature-humidity sensors.
- Power supply, solar panel, and power bank.
- 7” touchscreen with remote access for data monitoring.
Dendrostream | StF Code | StF Website

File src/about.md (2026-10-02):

---
title: About Title # will be overwritten by SEO.title below
date: 2023-09-21
layout: page
eleventyNavigation:
  key: main
  title: About # as it will appear in the nav
  order: 10 # order to display in the nav
seo:
  title: About Us # overrides 'title' above on both Page and META
  description: Meet the team
  image:
---

## Vision

*Sensing the Forest* brings an interdisciplinary team of artists and scientists together to work on a timely issue using an original approach to gaining knowledge about the connection between forests and climate change that can have a local, national and global impact. The democratisation of these tools is essential to progress in the field.

## Meet the team

{% wrap "px-2 mt-8 rounded-lg pb-2 border border-gray-300 bg-gray-200" %}

{% columns %}

{% cols "bg-gray-100 rounded-lg" %}

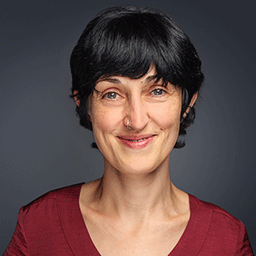
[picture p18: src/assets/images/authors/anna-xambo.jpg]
Photo of Anna Xambó


[Dr Anna Xambó (PI, Queen Mary University of London, C4DM)](https://annaxambo.me/)

Anna Xambó is a researcher and musician. Her research and practice focus on building and evaluating interactive music systems for music creation and performance using human-computer interaction research. She is a Senior Lecturer in Sound and Music Computing and a member of the Centre for Digital Music (C4DM) at School of Electronic Engineering and Computer Science (EECS), Queen Mary University of London.

{% endcols %}

{% cols "bg-gray-100 rounded-lg" %}

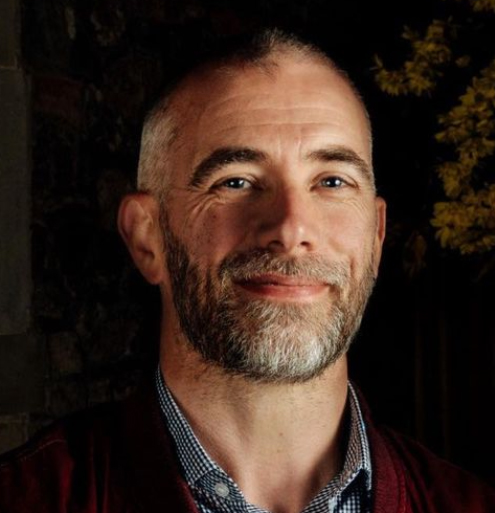
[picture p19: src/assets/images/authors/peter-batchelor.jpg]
Photo of Peter Batchelor


[Dr Peter Batchelor (CI, De Montfort University, MTI2)](https://peterb.dmu.ac.uk/)

Peter Batchelor is a Senior Lecturer and Programme Leader in Music Technology, and member of the Music, Technology and Innovation - Institute of Sonic Creativity (MTI2) at De Montfort University, Leicester.  His creative activities encompass a range of electroacoustic composition and sound-making work, including radiophonic documentary, live-electronics and improvisation, multimedia and large-scale multi-channel installation work. Research interests that arise from this practice include: aural landscape construction in sonic arts practice; sound spatialisation/immersion; theories of space; place and listening as they pertain to sound; audience engagement and public art.

{% endcols %}

{% endcolumns %}

{% columns %}

{% cols "bg-gray-100 rounded-lg" %}

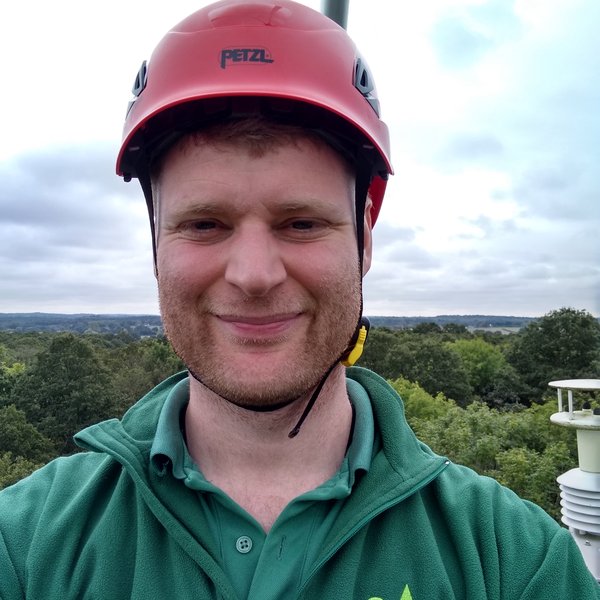
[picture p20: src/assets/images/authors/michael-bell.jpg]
Photo of Michael Bell


[Dr Michael Bell (CI, Forest Research)](https://www.forestresearch.gov.uk/staff/mike-bell/)

Mike Bell is Climate Scientist at Forest Research. Mike supports research at the Straits Inclosure long-term carbon dioxide flux monitoring site, helping to maintain sensors and data acquisition systems. As well as this, he is involved with routine data collection for the Environmental Change Network site and the ICP forests “Level II” programme. For both of these programmes, he is responsible for running the associated automated weather stations at Forest Research sites. Mike joined Forest Research as an Environmental Research Assistant in the Climate Change group in 2018 after obtaining a PhD in Environmental Science from the University of Reading. His PhD research focussed on the ecohydrology of blanket peatlands and their sensitivity to climate change.

{% endcols %}

{% cols "bg-gray-100 rounded-lg" %}

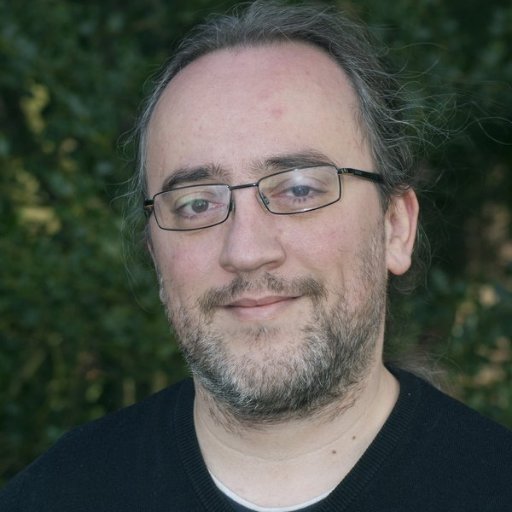
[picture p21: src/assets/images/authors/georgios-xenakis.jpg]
Photo of Georgios Xenakis


[Dr Georgios Xenakis (CI, Forest Research)](https://www.forestresearch.gov.uk/staff/georgios-xenakis/)

Georgios Xenakis' work focuses on measuring the carbon, water and energy balances of upland Sitka spruce plantations. Using micrometeorological techniques and eco-physiological process-based models, George quantifies the effect forest management has on carbon dynamics. George is also the manager of the Harwood Forest GHG monitoring site. His other research focuses on the drought effect on trees, both on the ecosystem and individual tree scale. George currently leads a manipulation experiment investigating the physiology of young trees during the recovery from drought.

{% endcols %}

{% endcolumns %}

{% columns %}

{% cols "bg-gray-100 rounded-lg" %}

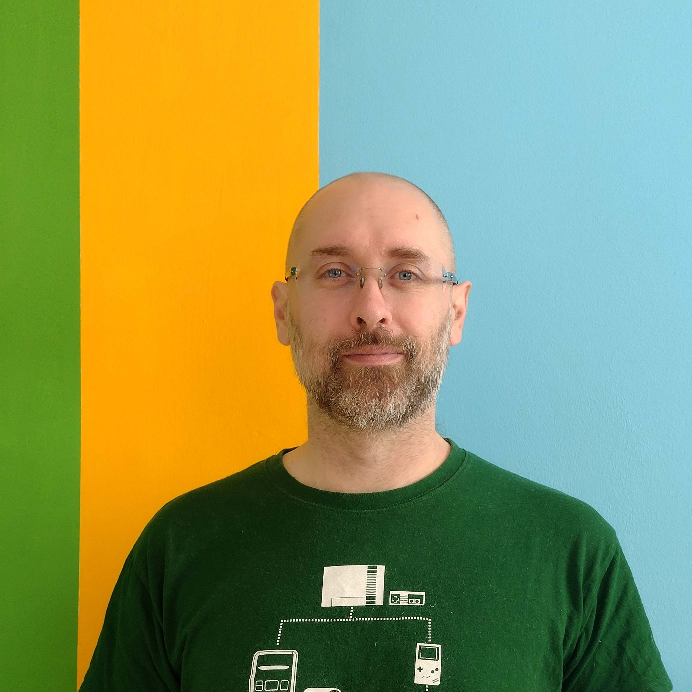
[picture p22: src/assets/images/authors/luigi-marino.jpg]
Photo of Luigi Marino


[Dr Luigi Marino (Research Fellow in Sound and Music Computing, Queen Mary University of London, C4DM)](http://www.luigimarino.net/)

Luigi Marino's work focuses on networks able to display relationships between human and nonhuman actors, and especially on how intuitive decisions can derail a pre-existing order. He is an active improvisor performing on both electronic media and percussion, in particular zarb and bowed custom cymbals extended with DIY portable circuits.

{% endcols %}

{% cols "bg-gray-100 rounded-lg" %}

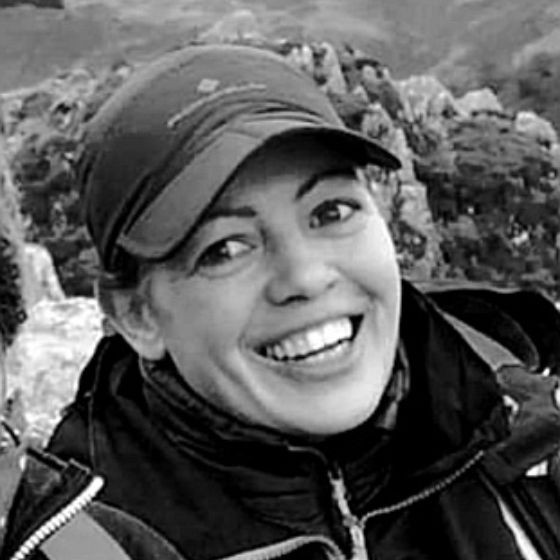
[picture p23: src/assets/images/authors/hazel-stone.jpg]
Photo of Hazel Stone


[Hazel Stone (Forestry England)](https://uk.linkedin.com/in/hazelstone)

Hazel Stone is the National Curator of Contemporary Art at Forestry England. Award-winning curator Hazel Stone has an established career that spans curating and commissioning contemporary art in the landscape, exhibition design, artist development, and learning. Her portfolio includes roles such as Curator of the Sidney Cooper Gallery, Director of Curious Planet, Lecturer and Arts Development Manager for the North of England for Forestry England, as well as Curator for Grizedale Forest. From 2016 to 2023, Hazel led the art programme for one of the largest outdoor galleries in the UK at Grizedale Forest, with over 50 sculptures in the landscape, maintaining and developing strategic partnerships to grow this nationally significant collection. She has initiated and supported a range of projects across the UK and internationally, bringing a wealth of experience, making her a driving force in the intersection of art, nature, and engagement. This expertise continues in her current role as National Curator of Contemporary Art for Forestry England, spearheading the development of contemporary art, architecture, and innovation in the nation’s forests through new commissions, publications, partnerships, residency programmes and touring exhibitions.

{% endcols %}

{% endcolumns %}

{% columns %}

{% cols "bg-gray-100 rounded-lg" %}

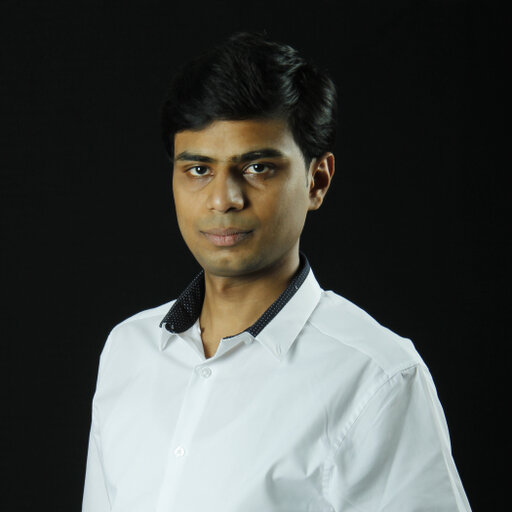
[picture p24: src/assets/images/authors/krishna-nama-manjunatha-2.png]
Photo of Krishna Nama Manjunatha


[Dr Krishna Nama Manjunatha (CI, De Montfort University, Emerging Technologies Research Centre)](https://www.dmu.ac.uk/about-dmu/academic-staff/technology/krishna-nama-manjunatha/krishna-nama-manjunatha.aspx)

Krishna Nama Manjunatha is a Senior Lecturer in Micro and Nano Electronics at De Montfort University. Krishna is interested in synthesis, development, and characterisation of nanoscale materials and their applications in emerging areas of electronics as well as in the growth of silicon nanostructures and its application in charge storage (memory and Li-Ion batteries) and charge generation (photovoltaics).

{% endcols %}

{% cols "bg-gray-100 rounded-lg" %}

Photo of Ashok Karavadra

[Ashok Karavadra (Senior Technician, De Montfort University)](https://uk.linkedin.com/in/ashok-karavadra-b1aa3a16a)

Ashok Karavadra is a Senior Technician at De Montfort University.

{% endcols %}

{% endcolumns %}

{% columns %}

{% cols "bg-gray-100 rounded-lg" %}

Photo of Danielle Grimsey

[Danielle Grimsey (Forestry England)](https://uk.linkedin.com/in/danielle-grimsey-b68a4827a)

Danielle Grimsey is the Visitor Services Manager at Alice Holt Forest and works alongside Max Gravestock. With her main focus being on visitors, her role combines her love for the outdoors and a commitment to providing visitors with an immersive and unforgettable connection to nature. Beyond the trees and trails, Danielle is passionate about creating opportunities for educational exploration, developing a deeper understanding and appreciation for the diverse ecosystems within our forest which is why she is excited to be a part of this project. Danielle started her role in September 2023 and still has lots to learn about how we can tell the beautiful, historical story of Alice Holt Forest.  

{% endcols %}

{% cols "bg-gray-100 rounded-lg" %}

Photo of Max Gravestock

[Max Gravestock (Forestry England)](https://uk.linkedin.com/in/max-gravestock-a7995a1b3)

Max Gravestock is the Site Manager at Alice Holt Forest (Forestry England) managing over 260 hectares of woodland at a busy visitor site that sees over 450,000 visitors a year. While Danielle focuses on the people and visitors, Max focuses on the site and its features including but not limited to: Mixed woodlands, Ponds, Meadows, Streams, Walking and cycling trails, play areas, and much more. Max's passion has always been in countryside management and finds great joy in starting an ambitious project, managing the works (or issues!) throughout and seeing the end product not only for the benefit of the site and its inhabitants but also the visitors who can enjoy and learn from the project and will go on to share what they have seen or learnt to others. Max has worked at Alice Holt for about 2.5 years now and still has much more to learn from this site with a rich history dating back to the Roman era, and is always looking for ways to tell the site's story in new and interesting ways.

{% endcols %}

{% endcolumns %}

{% columns %}

{% cols "bg-gray-100 rounded-lg" %}

Photo of Nick Wardlaw

[Nick Wardlaw (Forestry England)](https://uk.linkedin.com/in/nick-wardlaw-960251119)

Nick Wardlaw is the District Recreation Manager coving Visitor Centres in Forestry England’s South District. Nick works closely with Max Gravestock and Danielle Grimsey on how we can improve our offer for visitors and how they connect with our Forest at Alice Holt. Nick has been with Forestry England for 10 years working in both habitat conservation, and for the last four years his focus has been on connecting visitors with the forests. He takes great joy in knowing that the team’s work helps over a million people a year to learn to love and care for the outdoors environment.

{% endcols %}

{% cols "bg-gray-100 rounded-lg" %}

Photo of Johana Knowles

[Johana Knowles (Forestry England)](https://uk.linkedin.com/in/johana-knowles-51602722b)

Johana Knowles is a Visitor Services Officer at the Alice Holt Forest. Johana works at Alice Holt Forest in the Visitor Centre and is very interested in improving how to communicate to the Alice Holt's visitors through on site interpretation and digital media. Alice Holt has a fascinating social and ecological history that she thinks enhances a visitor’s experience of this place. We are still learning how to tell this story but she believes artistic intervention is an important part of achieving that. Johana comes from an arts background and is currently completing a masters in Illustration at Kingston University. Her art practice seeks to foster a sense of shared identity through place. She wants to tell stories in exciting and dynamic ways, in the hope of changing the way people think about the world for the better.

{% endcols %}

{% endcolumns %}

{% columns %}

{% cols "bg-gray-100 rounded-lg" %}

Photo of Matthew Wilkinson

[Dr Matthew Wilkinson (Advisor, Forest Research)](https://www.forestresearch.gov.uk/staff/matthew-wilkinson/)

Matt Wilkinson is a Programme Manager of the Natural Capital Ecosystem Assessment (NCEA),  has been Co-Investigator of the project until January 2024 and is currently a project advisor. The focus of his research is to improve our understanding of forest carbon and greenhouse gas (GHG) balances and how they may be impacted by management, environmental and climate change. Matt’s particular work focuses on using a combination of surface flux techniques across a range of scales to understand the processes controlling C and GHG cycling within forest ecosystems. In addition to leading several GHG and forest monitoring related projects, he has managed the Straits Flux Research Site within the Alice Holt Research Forest for > ten years. Matt is also interested in developing new techniques and sensors for trace gas flux measurements and forest monitoring. Matt joined Forest Research in 2001. He graduated from the University of Wales, Aberystwyth in 1995 with a BSc (Hons) in Agriculture and the Environment and then obtained an MSc in Crop Production in the Changing Environment in 1996 from the University of Essex. He completed his PhD by Publication at the University of Portsmouth.

{% endcols %}

{% cols "bg-gray-100 rounded-lg" %}

Photo of Kok Ho Huen

[Kok Ho Huen (Advisor, Queen Mary University of London, Electronics Lab)](https://www.qmul.ac.uk/eecs/people/profiles/huenho.html)

Kok Ho Huen is Electronics Teaching Lab Manager at QMUL and is a Technical Advisor of the project.

{% endcols %}

{% endcolumns %}

{% columns %}

{% cols "bg-gray-100 rounded-lg" %}

Photo of Gerard Roma

[Dr Gerard Roma (Advisor, University of West London)](https://www.uwl.ac.uk/staff/gerard-roma)

Gerard Roma has extensive experience in research and development in the field of sound and music computing and is a Technical Advisor of the project. He is also a practitioner in electronic and computer music. His research interests include audio analysis and synthesis, digital musical instruments, intelligent audio processing, audio source separation and environmental sound recognition.

{% endcols %}

{% cols "bg-gray-100 rounded-lg" %}

Photo of Frederic Font

[Dr Frederic Font (Advisor, Universitat Pompeu Fabra)](https://ffont.github.io/)

Frederic Font is a senior researcher at Phonos, a pioneering centre in the field of music technology research associated with the Music Technology Group of Universitat Pompeu Fabra, Barcelona, and is a Technical Advisor of the project. At the Music Technology Group, he leads the Freesound project and all Freesound-related research.

{% endcols %}

{% endcolumns %}

{% columns %}

{% cols "bg-gray-100 rounded-lg" %}

Photo of Aleksander Skutnik

[Aleksander Skutnik (Queen Mary University of London, Computer Science)](https://www.linkedin.com/in/aleksander-skutnik-1a05a625a/)

Aleksander Skutnik is a BSc Computer Science final year student at Queen Mary University of London. For his final year project, he has decided to undertake a research based topic within the Sensing the Forest project under the supervision of Dr Anna Xambó and Kok Ho Huen. His areas of interest and academic experience include probabilistic algorithms and risk analysis, as well as research experience in cognitive and sociocultural areas of psychology. Aleksander also has experience in community organising, advocacy and charity work for a range of organisations which include event and campaign planning.

{% endcols %}

{% cols "bg-gray-100 rounded-lg" %}

Photo of Shuoyang Zheng

[Shuoyang Zheng (Queen Mary University of London, AIM, C4DM)](https://jasperzheng.cc/)

Shuoyang Zheng is a PhD student at the Centre for Digital Music (C4DM), Queen Mary University of London. His research is in the field of explainable AI for musical audio synthesis. His long-term research goal focuses on developing interactive and understandable AI systems that facilitate musical creation and expression, and on understanding how these technological advances impact artistic practices. He is equally interested in the aesthetical and ethical implications inherent to the development of AI.

{% endcols %}

{% endcolumns %}

{% columns %}

{% cols "bg-gray-100 rounded-lg" %}

Photo of Stanley Parker

[Stanley Parker (Queen Mary University of London, Creative Computing)](https://www.linkedin.com/in/stanley-parker-43113425a)

Stanley Parker is a BSc Creative Computing student at Queen Mary University of London. He is creating an environmental monitoring module for his final year project and is working with the Sensing the Forest team to help make this happen and is being supervised for his project by Dr Anna Xambó and Kok Ho Huen. His areas of experience include sound design and generative audio, interactive media design, web programming, working with sensors and data mapping. Stanley also has an interest in music and audio production, conservation and general use of computers and other digital media in association with the natural world.

{% endcols %}

{% cols "bg-gray-100 rounded-lg" %}

Photo of NING LIU

[Ning Liu (Queen Mary University of London, Electronic Engineering)](https://www.linkedin.com/in/ning-liu-2969103b3/)

Ning Liu is the final year student in BSc(Eng)FT Electronic Engineering(with BUPT) at Queen Mary University in London. Under the supervision of Dr. Anna Xambó and Dr. Luigi Marino, she chose to take a study on the evaluation of MEMS microphones in the "Sensing the Forest" project as the last year's research topic. Her fields of interest and academic experience include interactive algorithms and communication analysis, as well as research experience in Arduino installation and cloud connection.

{% endcols %}

{% endcolumns %}

{% columns %}

{% cols "bg-gray-100 rounded-lg" %}

Photo of Mahmoud Elmokadem

[Mahmoud B. Elmokadem (De Montfort University, School of Engineering and Sustainable Developments)](https://www.linkedin.com/in/mahmoud-b-elmokadem-478617174)

Mahmoud B. Elmokadem is a PhD Researcher and Part-Time Lecturer in Mechatronics Engineering at De Montfort University, Leicester. His research focuses on the development of adaptive acoustic insulation panels designed to control sound with noise frequency adaptation capabilities. Mahmoud has a keen interest in building mechatronic systems and integrating advanced technologies to solve complex engineering problems.

{% endcols %}

{% cols "bg-gray-100 rounded-lg" %}

Image of Ireti Olowe

[Dr Ireti Olowe (Advisor, Creative Computing Institute, University of the Arts London)](https://missnommer.com/)

Ireti’s background, training and experience is in creativity support tools (CSTs) for audiovisual expression and performance. She has led industry research projects in games, virtual and urban experience, Web3, Internet of Things (IoT), HealthTech, FinTech, digital twins, digital agriculture, and smart cities, contributing expertise in human-computer interaction (HCI) and user experience (UX). Ireti is currently a research fellow at UAL’s Creative Computing Institute working on the AHRC funded Transforming Collections discovery project for the Towards a National Collection program. Her current research focuses on user interfaces that enable humans, facilitated by machine learning, to interrogate and manage museum-collections-as-data.

{% endcols %}

{% endcolumns %}

{% columns %}

{% cols "bg-gray-100 rounded-lg" %}

Photo of Subhash Arockiadoss

[Subhash Arockiadoss (De Montfort University, Mechatronics and Robotics)](https://www.linkedin.com/in/subhash-arockiadoss-2092b8171/)

Subhash Arockiadoss is a Robotics Engineer with a strong track record in designing and developing autonomous systems, sensor integration, and real-time robotic applications. Having recently completed his MSc in Mechatronics and Robotics at De Montfort University, Subhash brings hands-on experience with cutting-edge technologies such as ROS (Robot Operating System), SLAM (Simultaneous Localization and Mapping), and embedded systems like Jetson Nano and Raspberry Pi. His expertise has been applied to various industrial projects, including: Healthcare automation robots (Service Robot and Disinfect Robot), Agricultural robot for crop maintenance and Logistics robot for industrial applications. In the Sensing the Forest project, Subhash leverages his experience in robotics, sensor networks, and data analysis to contribute to the innovative use of environmental data. His goal is to raise awareness about the critical connection between forests and climate change by integrating cutting-edge robotic and sensing technologies.

{% endcols %}

{% cols "bg-gray-100 rounded-lg" %}

Photo of Xinyue Xu

Xinyue Xu (Queen Mary University of London, Sound and Music Computing)

Xinyue Xu is a MSc Sound and Music Computing student in EECS at Queen Mary University of London. She participates in the "Sensing the Forest" project, focusing on research in parameter mapping sonification and interactive music systems and under the supervision of Dr. Anna Xambó. Her research interests center on translating meteorological sensor data into sound and enhancing the understanding of the connection between forests and climate change through sonification techniques. She is also interested in immersive audio, 3D binaural sound rendering, and spatial hearing.

{% endcols %}

{% endcolumns %}

{% columns %}

{% cols "bg-gray-100 rounded-lg" %}

Photo of Andrés Sánchez Castrillón

[Andrés Sánchez Castrillón (Queen Mary University of London, Artificial Intelligence)](https://www.linkedin.com/in/andres-sanchez-59a8331a6/)

Andrés is a Master's student in Artificial Intelligence with a focus on Computer Vision. Originally from Medellín, Colombia, he has a background in software engineering and a keen interest in using AI to address environmental and sustainability challenges. Currently, he is starting to explore soundscape analysis for detecting patterns linked to climate change as part of his research.

{% endcols %}

{% cols "bg-gray-100 rounded-lg" %}

Photo of Tug O’Flaherty

[Tug O’Flaherty (Queen Mary University of London, Sound and Music Computing)](https://tugoflaherty.com)

Tug O’Flaherty is a Sound and Music Computing MSc student at Queen Mary University of London. Having previously undertaken a BSc (Hons) in Computer Science at Kingston University, he specialises in web and cross-platform mobile application development. Tug is excited to be applying his software development background to producing an interactive tool for the sonification and visualisation of climate and tree data within the Sensing the Forest project, under the direction of Dr Anna Xambó. He is passionate about climate change awareness and community-focussed initiatives, and keen to contribute his expertise in data mappings, music, and web development.

{% endcols %}

{% endcolumns %}

{% columns %}

{% cols "bg-gray-100 rounded-lg" %}

Photo of James Shortland

James Shortland (Queen Mary University of London, Data Science and Artificial Intelligence)

James Shortland is an MSc Data Science and Artificial Intelligence student at Queen Mary University of London. Originally from California, he is passionate about the outdoors and exploring AI’s potential to support nature conservation and combat climate change. He is contributing to the Sensing the Forest project through his work on Passive Acoustic Monitoring (PAM) under the supervision of Dr. Anna Xambó.

{% endcols %}

{% cols "bg-gray-100 rounded-lg" %}

Photo of Geetha Bommireddy

[Geetha Bommireddy (Advisor, Queen Mary University of London, The Maker Space)](https://www.qmul.ac.uk/eecs/people/profiles/bommireddygeetha.html)

Geetha Bommireddy is a Laboratory Technician & Materials Processing Research Technician at QMUL and a Technical Advisor of the project. Geetha is a graduate of Electronics and Communication Engineering. She has worked as a Technician for 10 years in sixth form college in London and joined QMUL in the year 2013. She has worked with many Masters and PhD students over the years in QMUL and loves what she does.

{% endcols %}

{% endcolumns %}

{% columns %}

{% cols "bg-gray-100 rounded-lg" %}

Photo of Nico García-Peguinho

[Nico García-Peguinho (Queen Mary University of London, C4DM)](https://www.linkedin.com/in/nico-g-p/)

Nico García-Peguinho is an artist and researcher based in the UK. His practice mainly explores algorithmic composition and sound art, with a recent focus on machine listening and data sonification. He is a member of the Sensing the Forest project and a first-year PhD student at the Centre for Digital Music (C4DM), Queen Mary University of London.

{% endcols %}

{% cols "bg-gray-100 rounded-lg" %}

Photo of Lianganzi Wang

[Lianganzi Wang (Queen Mary University of London, C4DM)](https://www.linkedin.com/in/nico-g-p/)

Lianganzi Wang is a PhD candidate in the School of Electronic Engineering and Computer Science at Queen Mary University of London, affiliated with the Centre for Digital Music (C4DM). Her current research focuses on machine learning for generative audio, timbre modeling, and multimodal interaction, dedicated to advancing the frontiers of intelligent music generation and interactive audio systems while exploring their innovative applications in creative expression.

{% endcols %}

{% endcolumns %}

{% columns %}

{% cols "bg-gray-100 rounded-lg" %}

Photo of Mazharia Rahman

[Mazharia Rahman (Advisor, Queen Mary University of London, EECS Finance)](https://www.qmul.ac.uk/eecs/people/profiles/rahmanmazharia.html)

Mazharia Rahman is an EECS Finance Assistant.

{% endcols %}

{% cols "bg-gray-100 rounded-lg" %}

Photo of Zainab Tarki

[Zainab Tarki (Advisor, De Montfort University, DMU Finance)](#)

Zainab Tarki was the Finance Officer of the project from September 2023 until December 2024.

{% endcols %}

{% endcolumns %}

<!-- {% columns %}

{% cols "bg-gray-100 rounded-lg" %}

{% endcols %}

{% cols "bg-gray-100 rounded-lg" %}

{% endcols %}

{% endcolumns %} -->

{% endwrap %}

## Advisory Board

{% wrap "px-2 mt-8 rounded-lg pb-2 border border-gray-300 bg-gray-200" %}

{% columns %}

{% cols "bg-gray-100 rounded-lg" %}

Photo of Mark Plumbley

[Professor Mark Plumbley (Professor of Signal Processing, EPSRC Fellow in "AI for Sound", University of Surrey)](https://www.surrey.ac.uk/people/mark-plumbley)

Prof Mark Plumbley's research concerns AI for Sound: using machine learning and signal processing for analysis and recognition of sounds. Mark's focus is on detection, classification and separation of acoustic scenes and events, particularly real-world sounds, using methods such as deep learning, sparse representations and probabilistic models. Mark has published over 400 papers in journals, conferences and books, including over 70 journal papers and the recent Springer co-edited book on Computational Analysis of Sound Scenes and Events. Much of Mark's research is funded by grants from EPSRC and EU, Innovate UK and other sources and currently holds an EPSRC Fellowship on "AI for Sound".

{% endcols %}

{% endcolumns %}

{% columns %}

{% cols "bg-gray-100 rounded-lg" %}

Photo of Louise Fedotov-Clements

[Louise Fedotov-Clements (Director of Photoworks, National Curator at Forestry England)](https://uk.linkedin.com/in/louise-fedotov-clements-4b25145)

Louise Fedotov-Clements is a senior leader in the arts with 20+ yrs international experience. She is currently the Director of Photoworks and leads the National Contemporary Art Programme at Forestry England across 1500 forests, where she has implemented the strategic direction, developing creative partnership projects, residencies, publications and events at the intersection of art, design, architecture, environment and ecology. Previously Louise was the Artistic Director of QUAD a centre for contemporary art and film for 20 years and Co-Founder Director of FORMAT International Photography Festival for 18 years, where Louise led major international commissions, events, festivals and engagement locally, nationally and worldwide.

{% endcols %}

{% endcolumns %}

{% columns %}

{% cols "bg-gray-100 rounded-lg" %}

Photo of Leigh Landy

[Professor Leigh Landy (Professor of Contemporary Music, Director of Music, Technology and Innovation - Institute for Sonic Creativity (MTI2), De Montfort University)](https://www.dmu.ac.uk/about-dmu/academic-staff/technology/leigh-landy/leigh-landy.aspx)

Prof Leigh Landy's research concerns electroacoustic musical production and musical studies: in particular, electroacoustic musicology, music dramaturgy, access to/facilitating the making of electroacoustic music, electroacoustic music in a cross-arts context, composition and devising practices. The major projects, beyond compositions, include analysis project and EARS 2 pedagogical project with the development of its Compose with Sounds software (+ associated publications including my recent book “Making Music with Sounds”). Leigh is editor of the international journal of music technology Organised Sound (Cambridge University Press) and author of over 100 articles and eight books.

{% endcols %}

{% endcolumns %}

{% endwrap %}

## Acknowledgements

Bret Battey (MTI2, DMU), Mike Baynham (University of Leeds), the Future Research Leaders 8 Cohort (DMU), Finella Bottomley (Leicester City Council), Tom Moore (DMU), Auwal Muktar Dodo (DMU), Gaia Rossetti (University of Nottingham), Lucy Gregson-Green (DMU), Meera Warrier (University of Leicester), Deborah Cartmell (DMU), Emma Vadher (DMU), Raffaella Villa (CEM, DMU), James Russell (CEM, DMU), Shushma Patel (CEM, DMU), Allan Taylor (LMS/CEM, DMU), James Andean (MTI2, DMU), Simon Atkinson (MTI2, DMU), John Young (MTI2, DMU), Janette Ratcliffe (DMU), Talent Acquisition Team (DMU), Krishna Vandra (TA, DMU), Emma Inch (TA, DMU), Ashiyah Banglawala (TA, DMU), Poonam Patel (HR, DMU), Monika Bednarczyk (HR, DMU), Val Milner (HR, DMU), Brijesh Thanki (CEM, DMU), Afzal Ghumra (DMU), Rachel Beeby (CEM, DMU), Lindsey Trent (CEM, DMU), Anne Galt (CEM, DMU), Zoe Cox (Forestry England), Jonathan McGloin (Forestry England), David Naylor (DMU), Shivalli (Leicester), Julie Macdonald (QMUL), Hayley Cork (QMUL), Sharon Cordin (QMUL), Jasmina Bolfek-Radovani (QMUL), Elzbieta Poplawska (QMUL), Jan Clarke (QMUL), Laura Kennard (QMUL), Annie Lewis (QMUL), Serena Bancroft (QMUL), Tania Sultana (QMUL), Jenny Martin (DMU), Gemma Goodman (DMU), Jack Diprose (Forestry England), David Wilkinson (QMUL).

<!---
{% wrap "bg-red-100 mt-4 border border-red-300 rounded-lg underline" %}

Text courtesy [Fillerama.io](http://fillerama.io/)

{% endwrap %}

## I hear the jury's still out on science.

Guy's a pro. It's a hug, Michael. I'm hugging you. Michael! I care deeply for nature. That's what it said on 'Ask Jeeves.' Across from where?

No, I did not kill Kitty. However, I am going to oblige and answer the nice officer's questions because I am an honest man with no secrets to hide. **Not tricks, Michael, illusions.** _Really?_ Did nothing cancel?

## There's so many poorly chosen words in that sentence.

No! I was ashamed to be SEEN with you. I like being with you. That's why you always leave a note! It's called 'taking advantage.' It's what gets you ahead in life. Steve Holt!

1. Michael!
2. What's Spanish for "I know you speak English?"
3. What's Spanish for "I know you speak English?"

### No… but I'd like to be asked!

I don't understand the question, and I won't respond to it. Oh, you're gonna be in a coma, all right. I don't criticize you! And if you're worried about criticism, sometimes a diet is the best defense.

- No… but I'd like to be asked!
- Guy's a pro.
- Well, what do you expect, mother?

That's what it said on 'Ask Jeeves.' I hear the jury's still out on science. It's called 'taking advantage.' It's what gets you ahead in life. Say goodbye to these, because it's the last time! Marry me.

No! I was ashamed to be SEEN with you. I like being with you. Well, what do you expect, mother? But I bought a yearbook ad from you, doesn't that mean anything anymore? Say goodbye to these, because it's the last time!

No! I was ashamed to be SEEN with you. I like being with you. First place chick is hot, but has an attitude, doesn't date magicians. No… but I'd like to be asked! I care deeply for nature.
--->

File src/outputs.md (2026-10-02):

---
title: Outputs Title # will be overwritten by SEO.title below
date: 2024-11-29
layout: page
eleventyNavigation:
  key: Outputs
  title: Outputs # as it will appear in the nav
  order: 8 # order to display in the nav
seo:
  title: Outputs # overrides 'title' above on both Page and META
  description: Academic, artistic and non-specialist outputs of the AHRC Sensing the Forest Project
  image:  outputs/starling-swarm.jpg # relative to /assets/images/
hero: graphic # options: carousel, graphic, video, split (text & image)
heroSettings:
  height:
    mobile: h-1/2 # options = h-1/1 (default = full screen), h-1/2, h-1/3, h-3/4, h-9/10, h-48 (12rem, 192px), h-56 (14rem, 224px), h-64 (16rem, 256px)
    desktop: # leave blank to inherit "mobile" height (default = full screen)
  headingText: # no heading text
  headingTextColor: text-gray-700 # text-gray-800 # default = text-white (can use any TailwindCSS text-[color]-[xxx])
  subheadingText: # no subheading text
  subheadingTextColor: # Leave empty to inherit headingTextColor or default (text-white) or use any text-[color]-[xxx]
  #buttonText: Apply # no button generated if left blank
  #buttonURL: https://de-montfort.onlinesurveys.ac.uk/sensing-the-forest-summer-school-application # full url required. Example: https://thisdomain.com/somepage/
  buttonTextColor: # leave blank to inherit from /src/_data/colors.buttonCustom or buttonDefault
  buttonBgColor:  # leave blank to inherit from /src/_data/colors.buttonCustom.bg or buttonDefault.bg
  bg:
    image: outputs/starling-swarm.jpg # image URL # image URL
    imagePosition: left # options = left, center, right
    imageOpacity: opacity-50 # options = opacity-25, opacity-50, opacity-75, opacity-100 (default)
    imageOpacityFilter: black # options = black or white (default) -> really depends on your background image

---

## Activities
 
<div class="float-left">
     <a aria-label="Link to Summer School" alt="Link to Summer School" href="/summer-school">
     <p class="text-center p-2">Summer School</p>
     </a>
     <a aria-label="Link to Summer School" alt="Link to Summer School" href="/summer-school">
     {% svg "sun-solid", "mt-2 ml-2 h-50 w-150" %}</a>
</div> 
<div class="float-left">    
     <a aria-label="Link to Seminars" alt="Link to Seminars" href="/seminars">
     <p class="text-center p-2">Seminars</p></a>
     <a aria-label="Link to Seminars" alt="Link to Seminars" href="/seminars">
     {% svg "comments-solid", "mt-1 mr-2 ml-2 h-50 w-150" %}</a>
</div>   
<div class="float-left">
  <a aria-label="Link to Media" alt="Link to Media" href="/media">
     <p class="text-center p-2">Media</p></a> 
     <a aria-label="Link to Media" alt="Link to Media" href="/media">
     {% svg "photo-film-solid", "mt-1 mr-2 ml-2 h-50 w-150 float-left" %}</a>
</div>

<br />

<pre>---</pre>

## Podcasts

* Zheng, Shuoyang (2025) [Sensing the Forest - Episode 2](https://soundcloud.com/sensingtheforest/podcast-ep2).
* Zheng, Shuoyang (2025) [Sensing the Forest - Episode 1](https://soundcloud.com/sensingtheforest/podcast-ep1).

<pre>---</pre>

## On the Press

* Wang, Lianganzi (31 December 2025) [How to listen to a forest](https://theconversation.com/how-to-listen-to-a-forest-268225), The Conversation.
* Xambó, Anna (1 November 2025) [Sensing the forest: exploring climate change through sound, AI and art](https://www.qmul.ac.uk/eecs/research/research-impact/case-study-sensing-the-forest/), Featured AI research case study series, EECS, QMUL.
* Wang, Lianganzi (9 September 2025) [审视林木：倾听气候代码——Sensing the Forest（感知森林）](https://mp.weixin.qq.com/s/52byCkEwKg63zC1B_h_FUQ) (Auditing the Arboreal: Listening to the Climate Code — Sensing the Forest), WeChat Official Account “女性艺术家” (Women Artists).
* Wang, Lianganzi (9 October 2025) [《聆听森林的脉动：声学叙事重塑生态感知》](https://mp.weixin.qq.com/s/rQ94gi-qFYV2b5PxY72iZQ) (Listening to the Forest’s Pulse: Acoustic Narratives Reshape Ecological Perception), WeChat Official Account “艺术学人” (The Artologist).

<pre>---</pre>

## Papers

*	O’Flaherty, T. F., Elmokadem, M. B., Xu, X., Manjunatha, K. N., Roma, G., Xenakis, G., Xambó, A., (2025) [“Sonification Mappings for Sensing Tree Stress: A DIY Approach”](https://zenodo.org/records/17642480). Proceedings of the Web Audio Conference 2025 (WAC 2025). Ircam/Mozilla, Paris, France. [\[Companion webpage\]](/wac2025)

<pre>---</pre>

## Abstracts

* García-Peguinho, N., Kelly, D., Navaratnarajah, M., Chockler, H., Xambó, A. (2025) ["Validating Few-shot Bird Vocalisation Detection through Causal Explanations"](/assets/pdf/ReX_StF_DMRN_PosterAbstract.pdf), DMRN+20, 2025, King’s College London, London, UK.
* Xambó, Anna; Batchelor, Peter; Marino, Luigi; Roma, Gerard; Bell, Mike; and Xenakis, George (2025). [Soundscape-based music and creative AI: Insights and promises](https://qmro.qmul.ac.uk/xmlui/bitstream/handle/123456789/110219/Xambo%20Soundscape-based%20music%202025%20Accepted.pdf?sequence=2), UK AI Research Symposium (UKAIRS) 2025, Newcastle, UK. 
* Marino, Luigi and Xambó, Anna (2024). [Developing DIY Solar-Powered, Off-Grid Audio Streamers for Forest Soundscapes: Progress and Challenges](https://www.chime.ac.uk/s/21-Luigi-Marino-and-Anna-Xambo.pdf), Proceedings of the [CHIME Annual One-day Music and HCI Conference 2024](https://www.chime.ac.uk/chime-annual-conference-2024), Milton Keynes, UK.

<pre>---</pre>

## Posters

* García-Peguinho, N., Kelly, D., Navaratnarajah, M., Chockler, H., Xambó, A. (2025) ["Validating Few-shot Bird Vocalisation Detection through Causal Explanations"](/assets/pdf/ReX_StF_DMRN_Poster.pdf), DMRN+20, 2025, King’s College London, London, UK.
*	O’Flaherty, T. F., Elmokadem, M. B., Xu, X., Manjunatha, K. N., Roma, G., Xenakis, G., Xambó, A., (2025) [“Sonification Mappings for Sensing Tree Stress: A DIY Approach”](/assets/pdf/WAC-2025.pdf). Proceedings of the Web Audio Conference 2025 (WAC 2025). Ircam/Mozilla, Paris, France.
* Xambó, Anna; Batchelor, Peter; Marino, Luigi; Roma, Gerard; Bell, Mike; and Xenakis, George (2025). [Soundscape-based music and creative AI: Insights and promises](/assets/pdf/UKAIRS-2025.pdf), UK AI Research Symposium (UKAIRS) 2025, Newcastle, UK. 
* Bell, Mike; Batchelor, Peter; Marino, Luigi; Xenakis, George; Gravestock, Max; Grimsey, Danielle; Knowles, Johana; Stone, Hazel; Wardlaw, Nick; and Xambó, Anna (2024). [Sensing the Forest: combining artistic and scientific methods](/assets/pdf/ICOS-2024.pdf), [Integrated Carbon Observation System (ICOS) Science Conference 2024](https://www.icos-cp.eu/news-and-events/science-conference/icos2024sc), Versailles, France & Online.

<pre>---</pre>

## Technical reports

* Marino, Luigi (2026) [Building DIY Solar-Powered Audio Streamers: A Three-Phase Tutorial Series](
https://doi.org/10.17636/101124743). Edited by Anna Xambó. Queen Mary University of London. https://doi.org/10.17636/101124743
* Elmokadem, Mahmoud B., Manjunatha, Krishna N., Xenakis, George, Xambó, Anna (2026) [Environmental Parameters Sensing (EPS) Unit](https://doi.org/10.17636/101124744). Edited by Anna Xambó. Queen Mary University of London. https://doi.org/10.17636/101124744

<pre>---</pre>

## Final UG/MSc projects

<br />

### Final MSc projects

* Sánchez Castrillón, Andrés (2025) "Sound Analysis of Soundscapes" (Supervisor: Anna Xambó). Final Year Postgraduate Project 2024/25, Artificial Intelligence MSc, School of Electronic Engineering and Computer Science, Queen Mary University of London. 
* Shortland, James (2025) "A Comparison of Voice Activity Detection Models: A Reflection on How Data Quality Affects Model Success" (Supervisor: Anna Xambó). Final Year Postgraduate Project 2024/25, Data Science and Artificial Intelligence MSc, School of Electronic Engineering and Computer Science, Queen Mary University of London.
* Xu, Xinyue (2025) ["Sonic Forest: Mapping Environmental Sensor Data to Sound for Climate Engagement"](/2025/09/17/sonic-forest/) (Supervisor: Anna Xambó). Final Year Postgraduate Project 2024/25, Sound and Music Computing MSc, School of Electronic Engineering and Computer Science, Queen Mary University of London.
* O'Flaherty, Tug (2025) ["Dendrostream: Exploring Tree Stress and Climate Change Through Sonification and Visualisation"](/2025/12/23/dendrostream/) (Supervisor: Anna Xambó). Final Year Postgraduate Project 2024/25, Sound and Music Computing MSc, School of Electronic Engineering and Computer Science, Queen Mary University of London.

<br />

### Final UG projects

* Kassem, Haidar Chawki (2026) ["Classification of High-Risk Disturbance in the Peruvian Amazon"](/2026/10/01/classification-of-high-risk-disturbance-in-the-peruvian-amazon/) (Supervisors: Anna Xambó and Rory Hodgson). Final Year Undergraduate Project 2025/26, BSc FT Computer Science and AI, School of Electronic Engineering and Computer Science, Queen Mary University of London. Programme of Study: Computer Science & Artificial Intelligence.
* Rumpal, Dharma (2026) ["WILT: exploring climate awareness through solar powered kinetic art"](/2026/10/01/wilt-using-solar-powered-kinetic-art-to-communicate-climate-change/) (Supervisors: Kok Ho Huen and Anna Xambó). Final Year Undergraduate Project 2025/26, BSC FT Computer Science (EngC Pathway), School of Electronic Engineering and Computer Science, Queen Mary University of London. Programme of Study: BSc Computer Science.
* Liu, Ning (2025) "MEMS microphones: finding the optimal solutions for recording in silent scenarios" (Supervisors: Luigi Marino and Anna Xambó). Final Year Undergraduate Project 2024/25, BSc(Eng)FT Electronic Engineering programme, School of Electronic Engineering and Computer Science, Queen Mary University of London. 
* Parker, Stanley (2025) ["Creating an affordable environmental monitoring system for residential use"](/2025/08/16/viridi/) (Supervisors: Kok Ho Huen and Anna Xambó). Final Year Undergraduate Project 2024/25, BSc Creative Computing programme, School of Electronic Engineering and Computer Science, Queen Mary University of London. 
* Skutnik, Aleksander (2025) ["Art, Unplugged: In the search of a sustainable off-grid power solution for immersive art installations"](/2025/08/01/art-unplugged/) (Supervisor: Anna Xambó). Final Year Undergraduate Project 2024/25, BSc Computer Science programme, School of Electronic Engineering and Computer Science, Queen Mary University of London. 

<pre>---</pre>

## Presentations

* Xambó, Anna (December 10, 2025): [Sensing the Forest: A Multidisciplinary Exploration of Sound Data](/2025/12/10/presentation-at-jean-golding-institute-december-10-2025/), Turing Seminars, Wills Memorial Building, Jean Golding Institute, University of Bristol, Bristol, UK.
* Xambó, Anna (October 28, 2025): [Sensing the Forest: Exploring Climate Change Through Soundscape Datasets from DIY Streamers at Alice Holt Forest](/2026/03/10/presentation-at-freesound-day-october-28-2025/), Freesound Day, 28 October 2025, Online/Barcelona.
* Xambó, Anna (October 15, 2025). Invited Talk: [”Sensing the Forest”](/2025/10/15/presentation-at-aix-marseille-university-october-15-2025/). Aix-Marseille University - Master in Acoustics and Musicology, Marseille, France. Online.
* Xambó, Anna (May 28, 2025). Keynote: [Liveness as an Open Work: An Ongoing Live-Coding Algorithmic Journey](https://iclc.toplap.org/2025/catalogue/keynote/keynote-anna-xambo.html), 9th International Conference on Live Coding (ICLC2025), 27 May 2025 - 31 May 2025, Barcelona, Spain.
* Xambó, Anna and Batchelor, Pete (May 14, 2025). Guest Lecture: ["Sensing the Forest - UAL workshop". Computer and Data Science and AI](/2025/05/17/presentation-at-ual-may-14-2025/), UAL Creative Computing Institute, University of the Arts London, London, UK. 
* Xambó, Anna (February 28, 2025). Invited Talk: "Intersecting Sonic Arts & Computing: A Portfolio Journey". Music Engineering Forum. University of Miami, Miami, FL, USA. Online.
* Xambó, Anna and Marino, Luigi (October 23, 2024). Invited Talk: [”Sensing the Forest: Lessons Learned from our Artistic-Acoustic Intervention at the Alice Holt Forest”](/2024/10/23/presentation-at-aix-marseille-university-october-23-2024/). Aix-Marseille University - Master in Acoustics and Musicology, Marseille, France. Online.
* Xambó, Anna (November 14, 2023). Keynote: [”From NIME to NISE: Rethinking the design and evaluation of musical interfaces”](/2023/12/18/presentation-at-adc23-november-14-2023/). Audio Developer Conference 2023 (ADC23). London, UK.
* Xambó, Anna (October 25, 2023). Invited Talk: [”In the search for epistemological cross-pollination between forest research, HCI and SMC”](/2023/11/01/presentation-at-chime-october-25-2023/). CHIME network. Online.

<pre>---</pre>

## Artistic outputs

* Xambó, Anna (June 24, 2026). *[Sensing the Alice Holt Forest](https://nime.org/proc_music/nime2026_music_46/index.html)*, live performance. New Interfaces for Musical Expression 2026, 23 June 2026 - 26 June 2026, Rich Mix, London, UK.
* García-Peguinho, Nico (November 22, 2025). [Sensing the Alice Holt Forest](/2025/12/17/sensing-the-forest-for-ground-creative-coding-utrecht-november-22-2025/), live performance. Multispecies concert, Creative Coding Utrecht, Utrecht, The Netherlands.
* Xambó, Anna (November 19, 2025). *[Sensing the Alice Holt Forest](https://medias.ircam.fr/fr/media/7e0777e073adecc86766)*, live performance. Web Audio Conference 2025, IRCAM/Mozilla, Paris, France.
* Xambó, Anna (May 29, 2025). *[Sensing the Alice Holt Forest](https://iclc.toplap.org/2025/catalogue/performance/sensing-the-alice-holt-forest.html)*, live performance. 9th International Conference on Live Coding (ICLC2025), 27 May 2025 - 31 May 2025, Barcelona, Spain.
* Batchelor, Peter: *[Dendrophone](/exhibition/your-sonic-forest-dendrophone-peter-batchelor/)*. Sound installation. August 2024-July 2025, Alice Holt Forest, GU10 4LS, Farnham, UK.
* *[Your Sonic Forest: Hear Nature Speak through Sound Installations in Alice Holt Forest - Art Event - Online](/exhibition/)*. August 2024-July 2025, Online.
* *[Your Sonic Forest: Hear Nature Speak through Sound Installations in Alice Holt Forest - Art Event](/exhibition/your-sonic-forest-foreword/)*. 20 June, 11am-3pm, 2024. Alice Holt Forest, GU10 4LS, Farnham, UK.
  * [*Within and Between* | Rosa Sungjoo Park](/exhibition/your-sonic-forest-within-and-between-rosa-sungjoo-park/)
  * [*Dendrophone* | Peter Batchelor](/exhibition/your-sonic-forest-dendrophone-peter-batchelor/)
  * [*Streamers* | Luigi Marino](/exhibition/your-sonic-forest-streamer-luigi-marino/)
  * [*Remembering the Mighty Oak* | Kate Anderson](/exhibition/your-sonic-forest-remembering-the-mighty-oak-kate-anderson/)
  * [*Tree Museum* | Ed Chivers](/exhibition/your-sonic-forest-tree-museum-ed-chivers/)
  * [*Tread(LIGHTLY)* | Gabrielle Cerberville](/exhibition/your-sonic-forest-tread(lightly)-gabrielle-cerberville/)
  * [*The Walking Tree* | Bardia Hafizi](/exhibition/your-sonic-forest-the-walking-tree-bardia-hafizi/)
  * [*Resonant Grove* | Austin Blanton](/exhibition/your-sonic-forest-resonant-grove-austin-blanton/)
  * [*A tree listens to itself* | Miles Scharff](/exhibition/your-sonic-forest-a-tree-listens-to-itself-miles-scharff/)
  * [*Sound Gardening at Alice Holt* | Jordan Juras](/exhibition/your-sonic-forest-sound-gardening-at-alice-holt-jordan-juras/)
  * [*Leaves Echo* | Qianyi Rose Sun](/exhibition/your-sonic-forest-leaves-echo-qianyi-rose-sun/)
  * [*In touch* | Beccy Abraham](/exhibition/your-sonic-forest-in-touch-beccy-abraham/)

<pre>---</pre>

## Hardware

* Elmokadem, Mahmoud B.; Manjunatha, Krishna Nama; Xenakis, George; and Xambó Anna (2024-): [DIY tree talker (code)](https://github.com/sensingtheforest/Sensing-Unit-System-Code).

* Bell, Mike and James, Catrina (2024): [Customised Data Logger](/exhibition/your-sonic-forest-data-logger-mike-bell-and-catrina-james/).

* Marino, Luigi (2023-2025): [Streamers' hardware (code)](https://github.com/sensingtheforest/audio-streamer).
  * [Tutorial 1: Phase 1 - Setting up the streamers](/streamers/tutorial-1/).
  * [Tutorial 2: Phase 2 - A DIY Solar-Powered Home LAN Audio Streamer that Can Record Samples at Solar Times](/streamers/tutorial-2/).
  * [Tutorial 3: Phase 3 - A DIY Solar-Powered Audio Streamer that Can Record Samples at Solar Times](/streamers/tutorial-3/).
  * [3D models](/streamers/tutorial-3/#3d-printed-parts).

<pre>---</pre>

## Software

* Web app customised DIY tree talker (2024-). In preparation.

* Xambó, Anna; Roma, Gerard; Bell, Mike; Jones, Catrina; Batchelor, Peter; Marino, Luigi; et al. (2024): Max web client customised data logger. In preparation.

* Xambó, Anna; Roma, Gerard; Batchelor, Peter; Bell, Mike; Marino, Luigi; et al. (2024-): [Pd web client customised data logger](https://github.com/sensingtheforest/web-client-data-logger). In preparation.

* Xambó, Anna; Roma, Gerard and Bell, Mike (2024-): Web server (Express.js). Under development.

* Marino, Luigi (2023-2025): Streamers' software (Raspberry Pi platform).
  * [Tutorial 1: Phase 1 - Setting up the streamers](/streamers/tutorial-1/).
  * [Tutorial 2: Phase 2 - A DIY Solar-Powered Home LAN Audio Streamer that Can Record Samples at Solar Times](/streamers/tutorial-2/).
  * [Tutorial 3: Phase 3 - A DIY Solar-Powered Audio Streamer that Can Record Samples at Solar Times](/streamers/tutorial-3/).

* Skutnik, Alexander (2025): [Art Unplugged](https://github.com/askutnik/artunplugged). Python. 

* Parker, Stanley (2025): [Viridi](https://github.com/S-Parker03/Final-Year-Project---Viridi). C++.

* O'Flaherty, Tug (2025): 
  * [Dendrostream (frontend)](https://github.com/sensingtheforest/dendrostream). d3.js/p5.js.
  * [Dendrostream (backend)](https://github.com/sensingtheforest/dendrostream-api). Javascript.

<pre>---</pre>

## Datasets

* Marino, L., Batchelor, P., & Xambó Sedó, A. (2025). Sensing the Forest - Natural Soundscape Dataset (5-minute audio recordings streamer I (natural soundscape)).  
  *  On Zenodo:
      * Marino, L., Batchelor, P., & Xambó Sedó, A. (2025). Sensing the Forest - Natural Soundscape Dataset - Part 1/2 [Dataset]. Zenodo. https://doi.org/10.5281/zenodo.18909809
      * Marino, L., Batchelor, P., & Xambó Sedó, A. (2025). Sensing the Forest - Natural Soundscape Dataset - Part 2/2 [Dataset]. Zenodo. https://doi.org/10.5281/zenodo.18911328   
  - On Freesound:
    * [Pack: natural-soundscape-dataset](https://freesound.org/people/sensingtheforest/packs/42937/).

* Marino, L., Batchelor, P., & Xambó Sedó, A. (2025). Sensing the Forest - Installation Soundscape Dataset (5-minute audio recordings streamer II (sound installation)).
  - On Zenodo:
      * Marino, L., Batchelor, P., & Xambó Sedó, A. (2025). Sensing the Forest - Installation Soundscape Dataset - Part 1/2 [Dataset]. Zenodo. https://doi.org/10.5281/zenodo.18911584
      * Marino, L., Batchelor, P., & Xambó Sedó, A. (2025). Sensing the Forest - Installation Soundscape Dataset - Part 2/2 [Dataset]. Zenodo. https://doi.org/10.5281/zenodo.18911592 

  - On Freesound:
    * [Pack: installation-soundscape-dataset](https://freesound.org/people/sensingtheforest/packs/43504/) on Freesound.

* 1-minute JSON files from customised data logger. Ongoing.
* 30-minute JSON files from DIY tree talker. Forthcoming.

<pre>---</pre>

## Live streams (from streamers)

{% wrap "pl-3 mt-4 bg-indigo-100 border border-indigo-300 text-lg italic rounded-lg" %}

:fire: **Note**: This is a solar-powered system in the woods, which means it sometimes goes offline. 
:fire: **Attention**: We recommend Chrome or Firefox for an optimal experience.

{% endwrap %}

* [Natural soundscape](http://solid41.streamupsolutions.com:8010/) (streaming ended on 26 August 2025)
* [Sound installation](http://solid67.streamupsolutions.com:8063/) (streaming ended on 26 August 2025)

<pre>---</pre>

## Videos

<br />

### AHRC StF *Your Sonic Forest: The Exhibition* Playlist

:star: [AHRC Your Sonic Forest: The Exhibition Playlist](https://www.youtube.com/playlist?list=PLoMU4dVZn5UMNgk5uT2g2AOFqgCuPix29) :star:

* [Your Sonic Forest | The Exhibition](https://youtu.be/VmutJeu9INE) (10:58), The Sensing the Forest YouTube Channel. Published on 10 Mar 2025. Video recorded and edited by Shuoyang Zheng.
* [Your Sonic Forest | In touch | Beccy Abraham](https://youtu.be/C-MbfLbV9vg) (0:21), The Sensing the Forest YouTube Channel. Recorded on 20 Jun 2024. Video recorded by Shuoyang Zheng.
* [Your Sonic Forest | Leaves Echo | Qianyi Rose Sun](https://youtu.be/rQm9fYQlWac) (1:39), The Sensing the Forest YouTube Channel. Recorded on 20 Jun 2024. Video recorded by Shuoyang Zheng.
* [Your Sonic Forest | Data Logger | Mike Bell & Catrina James](https://youtu.be/OIY0ZzOScsY) (0:12), The Sensing the Forest YouTube Channel. Recorded on 20 Jun 2024. Video recorded by Shuoyang Zheng.
* [Your Sonic Forest | A tree listens to itself | Miles Scharff](https://youtu.be/gGFM6hIc2KA) (1:46),The Sensing the Forest YouTube Channel. Recorded on 20 Jun 2024. Video recorded by Shuoyang Zheng.
* [Your Sonic Forest | Resonant Grove | Austin Blanton](https://youtu.be/Seri4CeSIPQ) (1:01), The Sensing the Forest YouTube Channel. Recorded on 20 Jun 2024. Video recorded by Shuoyang Zheng.
* [Your Sonic Forest | The Walking Tree | Bardia Hafizi](https://youtu.be/FhehZJUwDs0) (0:53), The Sensing the Forest YouTube Channel. Recorded on 20 Jun 2024. Video recorded by Shuoyang Zheng.
* [Your Sonic Forest | Tread(LIGHTLY) | Gabrielle Cerberville](https://youtu.be/VgqhNuvJCtY) (1:25), The Sensing the Forest YouTube Channel. Recorded on 20 Jun 2024. Video recorded by Shuoyang Zheng.
* [Your Sonic Forest | Tree Museum | Ed Chivers](https://youtu.be/wyNkLs5y0yg) (0:59), The Sensing the Forest YouTube Channel. Recorded on 20 Jun 2024. Video recorded by Shuoyang Zheng.
* [Your Sonic Forest | Streamer | Luigi Marino](https://youtu.be/67sZidhHBdQ) (0:32), The Sensing the Forest YouTube Channel. Recorded on 20 Jun 2024. Video recorded by Shuoyang Zheng.
* [Your Sonic Forest | Dendrophone | Peter Batchelor](https://youtu.be/HYTKoBM6C0k) (1:31), The Sensing the Forest YouTube Channel. Recorded on 20 Jun 2024. Video recorded by Shuoyang Zheng.

<br />

### AHRC StF Summer School Video Presentations Playlist

:star: [AHRC StF Summer School Video Presentations Playlist](https://www.youtube.com/playlist?list=PLoMU4dVZn5UPXOKGwu9AxdXYPorWwrM2e) :star:

* [Summer School Artists - Sensing the Forest Summer School Presentation: Initial Prototypes](https://youtu.be/cuNWg0LoENU) (27:33), The Sensing the Forest YouTube Channel. Published on 23 May 2024.
* [Johana Knowles - Sensing the Forest Summer School Presentation: Placemaking and Audience](https://youtu.be/PVdjfxjYDIo) (9:53), The Sensing the Forest YouTube Channel. Recorded on 24 Apr 2024.
* [Hazel Stone - Sensing the Forest Summer School Presentation: Approaches to Creative Responses in the Landscape](https://youtu.be/EzGd2K_lBPI) (23:28), The Sensing the Forest YouTube Channel. Recorded on 11 Apr 2024.
* [Peter Batchelor - Sensing the Forest Summer School Presentation: Public Sound Installation Art](https://youtu.be/5lwzz32v5XU) (41:54), The Sensing the Forest YouTube Channel. Recorded on 25 Apr 2024.
* [Mike Bell - Sensing the Forest Summer School Presentation: Alice Holt Long-Term Carbon Dioxide Flux Monitoring Site](https://youtu.be/FqkD7AWdrhg) (19:14), The Sensing the Forest YouTube Channel. Recorded on 29 Feb 2024.
* [Nick Wardlaw - Sensing the Forest Summer School Presentation: An Introduction to Alice Holt Forest Centre](https://youtu.be/vqq-A8uAHZ4) (15:19), The Sensing the Forest YouTube Channel. Recorded on 29 Feb 2024.

<br />

### AHRC StF Understanding Data and Place Video Presentations Playlist

:star: [AHRC StF Understanding Data and Place Video Presentations Playlist](https://www.youtube.com/playlist?list=PLoMU4dVZn5UNSBLWp3VCcga0vkpNqPu-x) :star:

* [George Xenakis - Sensing the Forest Hands-on Demonstration: How a Tree Talker Works](https://youtu.be/uGEq9BrhNNw) (28:37), The Sensing the Forest YouTube Channel. Recorded on 13 Nov 2024.
* [George Xenakis - Sensing the Forest Presentation: Introduction to the Northern Research Station](https://youtu.be/Axs6DDR2PuM) (25:27), The Sensing the Forest YouTube Channel. Recorded on 12 Sep 2024.
* [Matt Wilkinson - Sensing the Forest Presentation: Introduction to the Alice Holt Research Forest](https://youtu.be/2twAW03Kjxc) (23:13), The Sensing the Forest YouTube Channel. Recorded on 17 Nov 2023.

<br />

### AHRC StF Seminar Series Video Presentations Playlist

:star: [AHRC StF Seminar Series Video Presentations Playlist](https://www.youtube.com/playlist?list=PLoMU4dVZn5UPXOKGwu9AxdXYPorWwrM2e) :star:

* [Liz O’Brien and Alice Eldridge - Sensing the Forest Seminar #3: Q&A moderated by Peter Batchelor](https://youtu.be/6TsRhxeyvxI) (20:36), The Sensing the Forest YouTube Channel. Recorded on 15 Nov 2023.
* [Alice Eldridge - Sensing the Forest Seminar #3: Tuning in to Soundscape Dynamical Complexity](https://youtu.be/uVFAjsKPASs) (35:06), The Sensing the Forest YouTube Channel. Recorded on 15 Nov 2023.
* [Liz O’Brien - Sensing the Forest Seminar #3: Sounds in and of the Forest: Can We Connect People to Nature Through Sound?](https://youtu.be/R9_aVdTCR-Q) (29:05), The Sensing the Forest YouTube Channel. Recorded on 15 Nov 2023.
* [Saloni Shah and Daniel Jones - Sensing the Forest Seminar #2: Q&A moderated by Peter Batchelor](https://youtu.be/VijwFCCqcQo) (14:49), The Sensing the Forest YouTube Channel. Recorded on 1 Nov 2023.
* [Daniel Jones (Jones/Bulley) - Sensing the Forest Seminar #2: Living Symphonies](https://youtu.be/6Q9WSQCWDnM) (36:08), The Sensing the Forest YouTube Channel. Recorded on 1 Nov 2023.
* [Saloni Shah - Sensing the Forest Seminar #2: How Information Design Can Save Forest Ecosystems](https://youtu.be/X17QTN6-9Fg) (30:33), The Sensing the Forest YouTube Channel. Recorded on 1 Nov 2023.
* [Ruth Jarman and Peter Sinclair - Sensing the Forest Seminar #1: Q&A moderated by Peter Batchelor](https://youtu.be/x8O7BEmsLHg) (24:30), The Sensing the Forest YouTube Channel. Recorded on 18 Oct 2023.
* [Peter Sinclair - Sensing the Forest Seminar #1: Locustream Open Microphones - Acoustic commons : a shared resource to renew listening](https://youtu.be/MBMupEfgu54) (27:55), The Sensing the Forest YouTube Channel. Recorded on 18 Oct 2023.
* [Ruth Jarman (Semiconductor) - Sensing the Forest Seminar #1: Worlds in Flux: Semiconductor](https://youtu.be/ybcRIX_kR8I) (29:05), The Sensing the Forest YouTube Channel. Recorded on 18 Oct 2023.

<br />

### Testimonials

* [StF QMUL EECS UG Projects 2024-25](https://youtu.be/YbqCNVtGH7Q) (2:48), The Sensing the Forest YouTube Channel. Published on 2 May 2025.

<br />

### MSc Presentations

* [MSc Final Project Presentation: Dendrostream by Tug F. O'Flaherty](https://youtu.be/PdX0l6dTxfI) (9:44), The Sensing the Forest YouTube Channel. Published on 21 August 2025.
* [MSc Final Project Presentation: Sonic Forest by Xinyue Xu](https://youtu.be/RUa0tish_Fs) (12:10), The Sensing the Forest YouTube Channel. Published on 21 August 2025.

<br />

<pre>---</pre>

## Interviews

<br />

### Interviews by Aleksander Skutnik with Artists who Work with Solar-Powered Solutions: Peter Batchelor, Sarah Hall

:star: [Interviews with Artists who Work with Solar-Powered Solutions](/tags/artistic-olar-powered-solutions/) :star:

* Skutnik, Aleksander (14 Mar 2025) [An Interview with Chris Meigh-Andrews](/2025/03/14/an-interview-with-chris-meigh-andrews/). The Sensing the Forest blog.
* Skutnik, Aleksander (10 Mar 2025) [An Interview with Sarah Hall](/2025/03/10/an-interview-with-sarah-hall/). The Sensing the Forest blog.
* Skutnik, Aleksander (8 Feb 2025) [An Interview with Peter Batchelor](/2025/02/08/an-interview-with-peter-batchelor/). The Sensing the Forest blog.

<br />

### Interviews by Hazel Stone with AHRC StF Summer School Artists: Bardia Hafizi, Ed Chivers, Qianyi Rose Sun, Gabrielle Cerberville, Austin Blanton, Miles Scharff, Kate Anderson, Jordan Juras, Rosa Sungjoo Park, Beccy Abraham

:star: [Interviews with AHRC StF Summer School Artists](/tags/meet-the-artists/) :star:

* Stone, Hazel (26 May 2024) [Meet the Artists - Beccy Abraham](/2024/05/27/meet-the-artists-beccy-abraham/). The Sensing the Forest blog.
* Stone, Hazel (26 May 2024) [Meet the Artists - Rosa Sungjoo Park](/2024/05/26/meet-the-artists-rosa-sungjoo-park/). The Sensing the Forest blog.
* Stone, Hazel (24 May 2024) [Meet the Artists - Jordan Juras](/2024/05/24/meet-the-artists-jordan-juras/). The Sensing the Forest blog.
* Stone, Hazel (20 May 2024) [Meet the Artists - Kate Anderson](/2024/05/20/meet-the-artists-kate-anderson/). The Sensing the Forest blog.
* Stone, Hazel (17 May 2024) [Meet the Artists - Miles Scharff](/2024/05/17/meet-the-artists-miles-scharff/). The Sensing the Forest blog.
* Stone, Hazel (15 May 2024) [Meet the Artists - Austin Blanton](/2024/05/15/meet-the-artists-austin-blanton/). The Sensing the Forest blog.
* Stone, Hazel (13 May 2024) [Meet the Artists - Gabrielle Cerberville](/2024/05/13/meet-the-artists-gabrielle-cerberville/). The Sensing the Forest blog.
* Stone, Hazel (10 May 2024) [Meet the Artists - Qianyi Rose Sun](/2024/05/10/meet-the-artists-qianyi-rose-sun/). The Sensing the Forest blog.
* Stone, Hazel (8 May 2024) [Meet the Artists - Ed Chivers](/2024/05/08/meet-the-artists-ed-chivers/). The Sensing the Forest blog.
* Stone, Hazel (6 May 2024) [Meet the Artists - Bardia Hafizi](/2024/05/06/meet-the-artists-bardia-hafizi/). The Sensing the Forest blog.

<br />

### Interviews by Anna Xambó and Luigi Marino with AHRC StF Seminar Series Speakers: Peter Sinclair, Saloni Shah, Jones/Bulley, Liz O’Brien and Alice Eldridge

:star: [Interviews with AHRC StF Seminar Series Speakers](/tags/seminar-series/) :star:

* Xambó, Anna and Marino, Luigi (27 March 2024) [An Interview with Jones/Bulley](/2024/03/27/an-interview-with-jones-bulley/). The Sensing the Forest blog.
* Xambó, Anna and Marino, Luigi (21 February 2024) [An Interview with Liz O'Brien](/2024/02/21/an-interview-with-liz-obrien/). The Sensing the Forest blog.
* Xambó, Anna and Marino, Luigi (5 February 2024) [An Interview with Alice Eldridge](/2024/02/05/an-interview-with-alice-eldridge/). The Sensing the Forest blog.
* Xambó, Anna and Marino, Luigi (14 January 2024) [An Interview with Peter Sinclair](/2024/01/14/an-interview-with-peter-sinclair/). The Sensing the Forest blog.
* Xambó, Anna and Marino, Luigi (5 December 2023) [An Interview with Saloni Shah](/2023/12/05/an-interview-with-saloni-shah/). The Sensing the Forest blog.

<pre>---</pre>

## Photo albums

* Zheng, Shuoyang (2024) [Sensing the Forest Summer School - Day 1](https://flickr.com/photos/200917075@N06/albums/72177720318062910), The Sensing the Forest Flickr account.
* Zheng, Shuoyang (2024) [Sensing the Forest Summer School - Day 2](https://flickr.com/photos/200917075@N06/albums/72177720318197655), The Sensing the Forest Flickr account.

<pre>---</pre>

## Promotional Leaflets & Posters

* [Dendrophone instructions poster](/assets/pdf/Dendrophone-Peter-Batchelor-instructions.pdf). Designed by Peter Batchelor, Geetha Bommireddy and Anna Xambó.
* [Your Sonic Forest leaflet](/assets/pdf/Your-sonic-forest-leaflet.pdf). Designed by Johana Knowles.
* [Your Sonic Forest poster](/assets/pdf/Your-sonic-forest-poster.pdf). Designed by Johana Knowles.
* [Your Sonic Forest survey poster](/assets/pdf/Your-sonic-forest-survey-poster.pdf). Designed by Johana Knowles.
* [Sensing the Forest at Alice Holt Forest leaflet](/assets/pdf/StF-Alice-Holt-Forest_A4_highres_V2.pdf). Designed by the Sensing the Forest Team.
* [Sensing the Forest at Northern Research Station leaflet](/assets/pdf/StF-Northern-Research-Station_A4_highres-V2.pdf). Designed by the Sensing the Forest Team.

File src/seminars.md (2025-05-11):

---
title: Seminars Title # will be overwritten by SEO.title below
date: 2023-09-21
layout: page
eleventyNavigation:
  key: Seminars
  parent: Outputs  
  title: Seminars # as it will appear in the nav
  order: 7 # order to display in the nav
seo:
  title: Seminars # overrides 'title' above on both Page and META
  description: Discover the 1st AHRC Sensing the Forest seminar series (Oct-Nov 2023)
  image: seminars/Sensing-the-Forest-Online-Seminar-Talks.jpg
---

The AHRC Sensing the Forest project is organising a series of three fortnightly online seminar talks with experts related to artistic, social and scientific interventions in the forest or other natural landscapes with a special focus on acoustic phenomena. The seminar series will include talks by Semiconductor, Peter Sinclair, Saloni Shah, Jones/Bulley, Liz O'Brien and Alice Eldridge.

<!-- {% wrap "mt-4 bg-indigo-100 border border-indigo-300 text-lg italic rounded-full text-left" %} -->

{% wrap "pl-3 mt-4 bg-indigo-100 border border-indigo-300 text-lg italic rounded-lg" %}

Many thanks for your interest in the seminar series. The first edition of the seminar series concluded with great success. We had a total of 275 registered attendees. You can:
:fire: Download the [poster of the seminar series](/assets/images/seminars/Sensing-the-Forest-Online-Seminar-Talks.jpg) :fire:
:fire: Watch the [video presentations playlist](https://youtu.be/ybcRIX_kR8I?list=PLoMU4dVZn5UPXOKGwu9AxdXYPorWwrM2e) :fire:
:fire: Read the [interviews with the seminar speakers](/tags/seminar-series/) :fire:
:fire: Leave comments / give likes to our [blog posts](/blog) & [Sensing the Forest YouTube channel](https://www.youtube.com/@sensingtheforest) :fire:
:fire: [Subscribe to our announce mailing list](https://groups.google.com/g/sensingtheforest-announce) (Ask to join the group) :fire:
<!-- * Provide us [feedback](https://de-montfort.onlinesurveys.ac.uk/sensing-the-forest-seminar-series-feedback). -->

{% endwrap %}

<!-- {% endwrap %} -->

## Wed, 15 Nov 2023 15:00 - 16:30 UK time

3rd Sensing the Forest Seminar: Liz O'Brien and Alice Eldridge

{% wrap "mt-4 bg-indigo-100 border border-indigo-300 text-lg italic rounded-full text-left" %}

:star: You can find more info and register for the free event on the [following Eventbrite link](https://www.eventbrite.com/e/sensing-the-forest-seminar-liz-obrien-and-alice-eldridge-tickets-745155689727) :star:

{% endwrap %}

<br />

### Liz O'Brien

#### Sounds in and of the Forest: Can We Connect People to Nature Through Sound?

Liz O'Brien will talk about the ecotones network which was interdisciplinary and brought together musicians, social scientists focused on health and wellbeing, conservation ecologist, and education to share knowledge and ideas. She will also touch on the ACCESS project which is trying to make social science accessible in tackling a range of environmental problems.
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

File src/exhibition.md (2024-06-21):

---
title: Online Exhibition # will be overwritten by SEO.title below
date: 2024-05-18
layout: page
eleventyNavigation:
  key: main
  title: Exhibition # as it will appear in the nav
  order: 3 # order to display in the nav
seo:
  title: Your Sonic Forest - Hear Nature Speak through Sound Installations in Alice Holt Forest
 # overrides 'title' above on both Page and META
  description: Art event - Thursday 20th June 11am-3pm, Alice Holt Forest (free entrance)
  image: exhibition/Peter-Batchelor-bird-boxes-speakers.jpg # relative to /assets/images/
hero: graphic # options: carousel, graphic, video, split (text & image)
heroSettings:
  height:
    mobile: h-1/1 # options = h-1/1 (default = full screen), h-1/2, h-1/3, h-3/4, h-9/10, h-48 (12rem, 192px), h-56 (14rem, 224px), h-64 (16rem, 256px)
    desktop: # leave blank to inherit "mobile" height (default = full screen)
  headingText: Your Sonic Forest
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

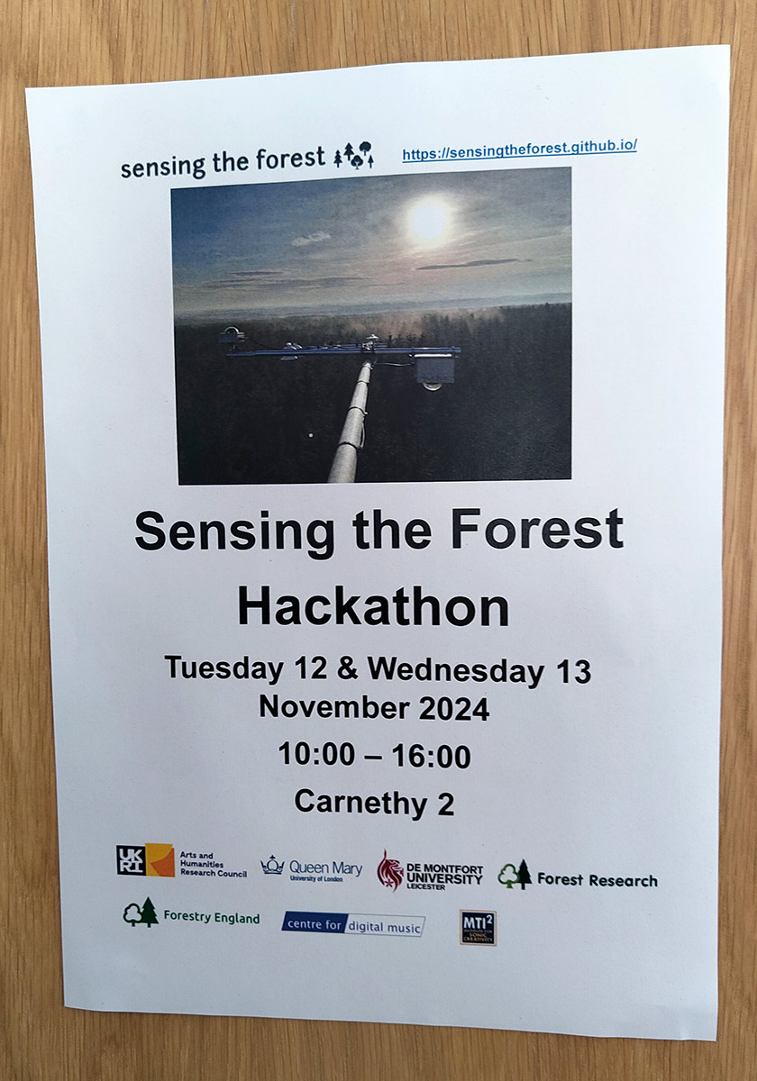
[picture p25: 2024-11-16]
src/assets/images/2024/11/poster.jpg

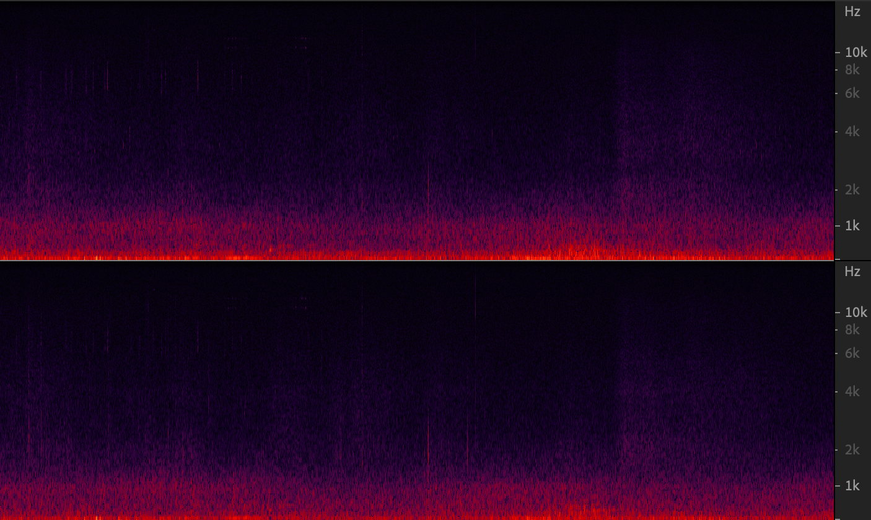
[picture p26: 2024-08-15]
src/assets/images/2024/08/2024-07-23-spectrogram-Alice-Holt-Lodge-Pond-facing-forest.png

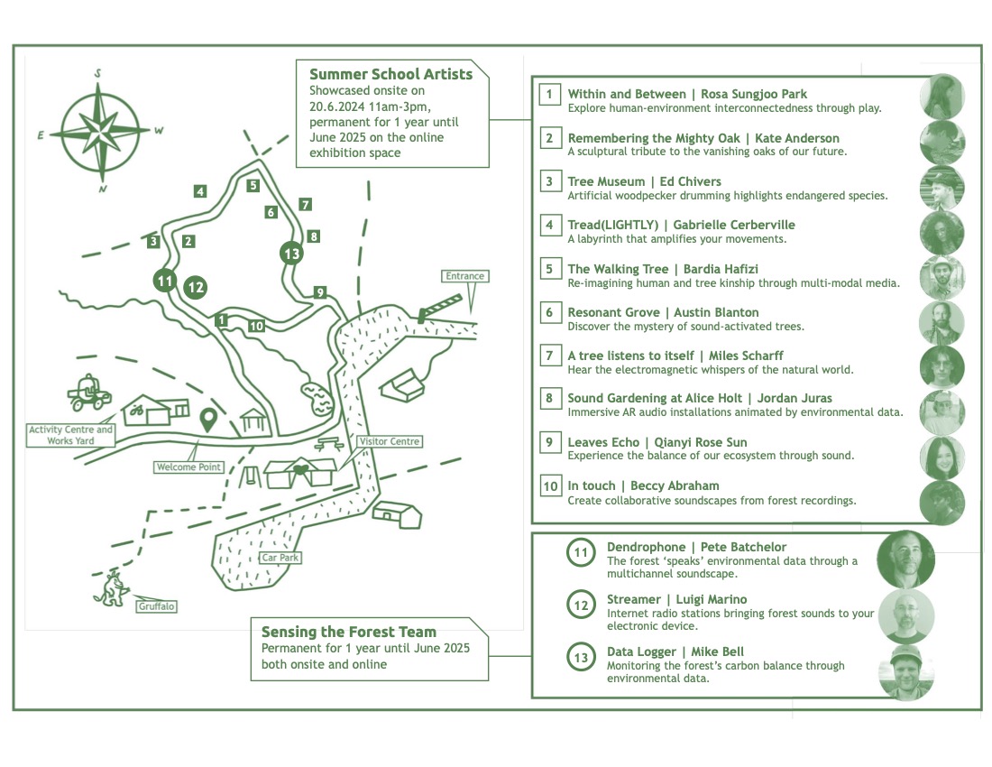
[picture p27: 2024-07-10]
src/assets/images/exhibition/Your-sonic-forest-leaflet-p2_design_by_Johana_Knowles.jpg

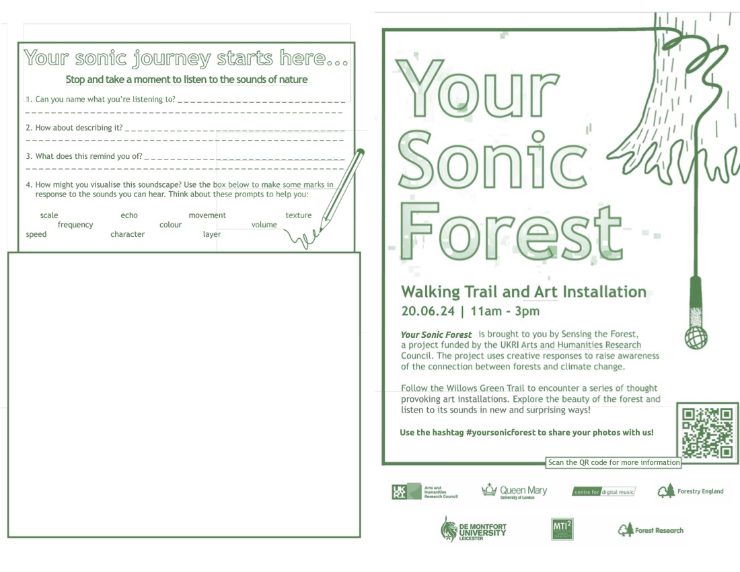
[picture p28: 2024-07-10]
src/assets/images/exhibition/Your-sonic-forest-leaflet-p1_design_by_Johana_Knowles.jpg

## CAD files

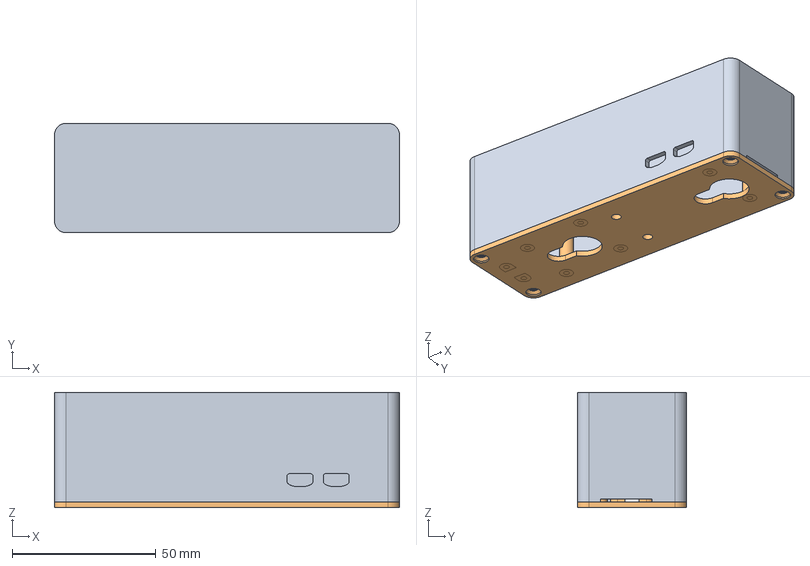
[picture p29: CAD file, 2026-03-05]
src/assets/3d-print/rpi0_ads1115_suction-cup.FCStd
120.0 x 38.0 x 40.0 mm
Top002
Bottom001

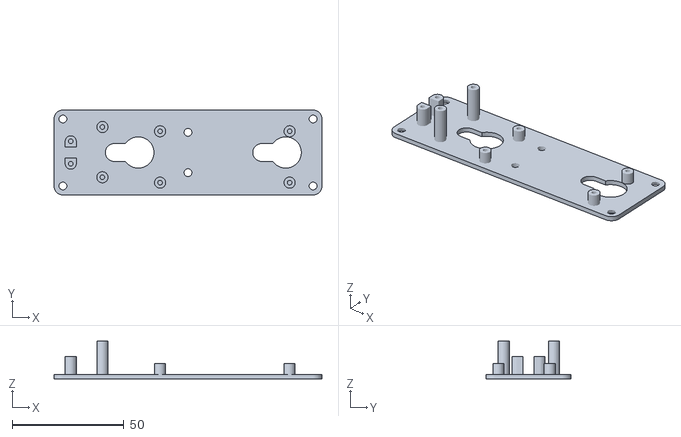
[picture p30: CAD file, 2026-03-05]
src/assets/3d-print/rpi0-case_ads1115_suction-cup_BOTTOM.stl
120.0 x 38.0 x 17.0

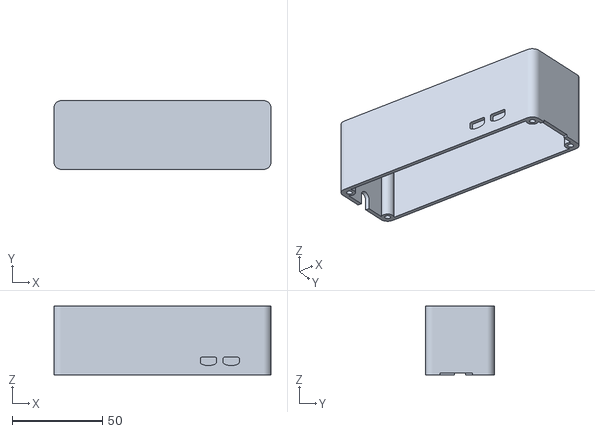
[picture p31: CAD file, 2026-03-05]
src/assets/3d-print/rpi0-case_ads1115_suction-cup_TOP.stl
120.0 x 38.0 x 38.0

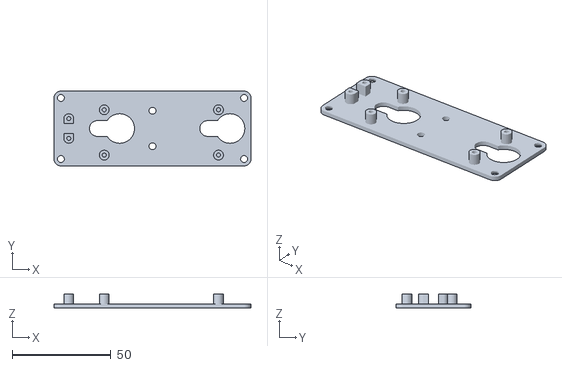
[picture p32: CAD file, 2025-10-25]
src/assets/3d-print/rpi0-case_suctioncap-1_BOTTOM.stl
100.0 x 38.0 x 7.00

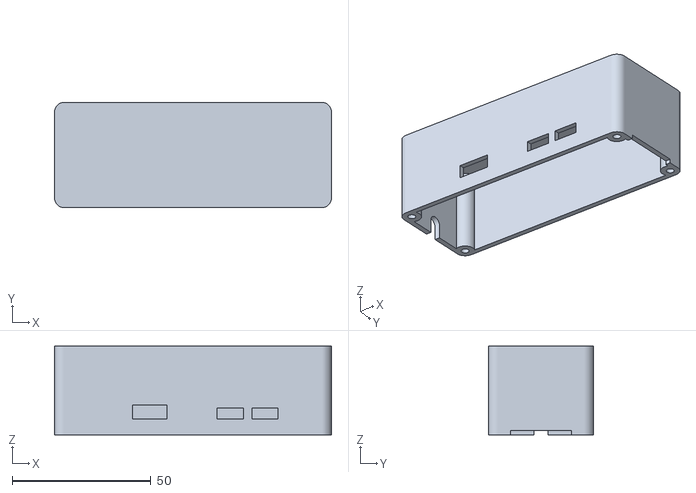
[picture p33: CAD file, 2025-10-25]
src/assets/3d-print/rpi0-case_suctioncap-1_TOP.stl
100.0 x 38.0 x 32.0

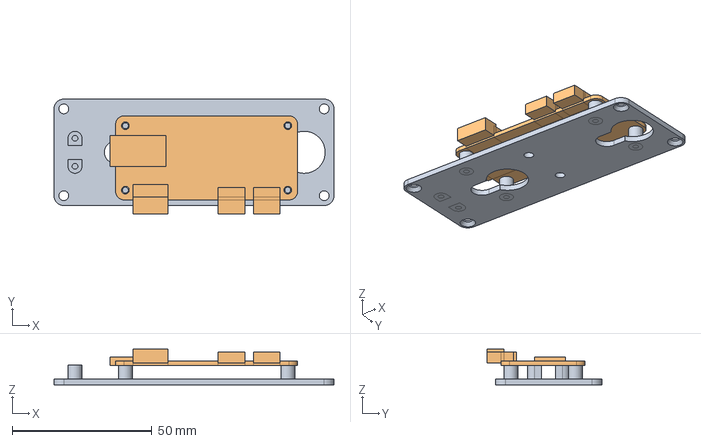
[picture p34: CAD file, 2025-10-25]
src/assets/3d-print/rpi-zero_suction-cup-1.FCStd
100.0 x 41.0 x 12.8 mm
Bottom

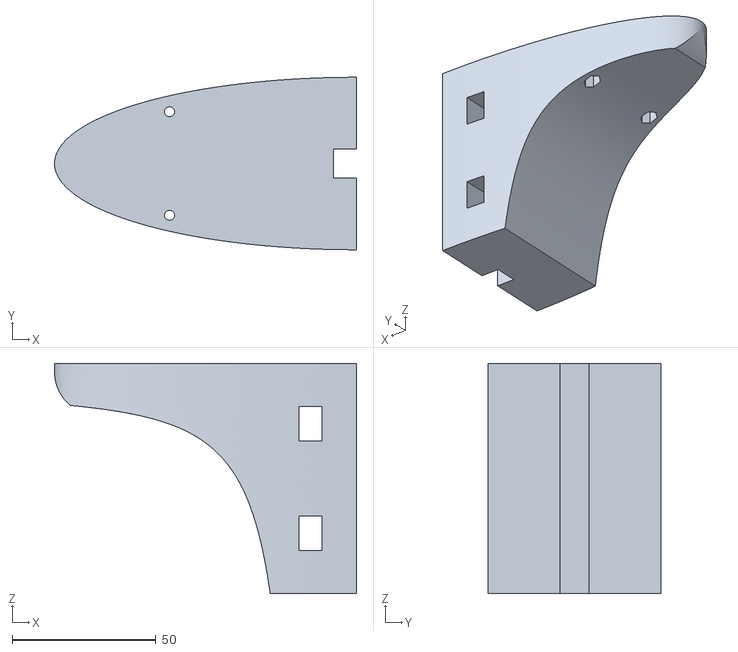
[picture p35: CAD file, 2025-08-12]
src/assets/3d-print/TreeShelf.stl
105.0 x 60.0 x 80.0

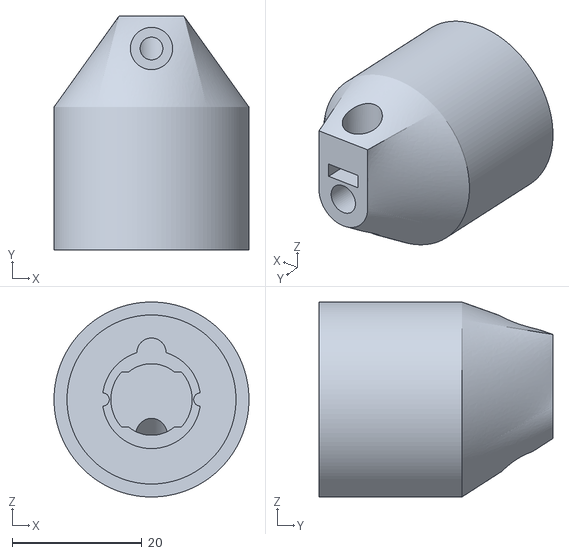
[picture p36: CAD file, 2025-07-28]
src/assets/3d-print/MicHolder_MEMS.stl
30.0 x 36.0 x 30.0

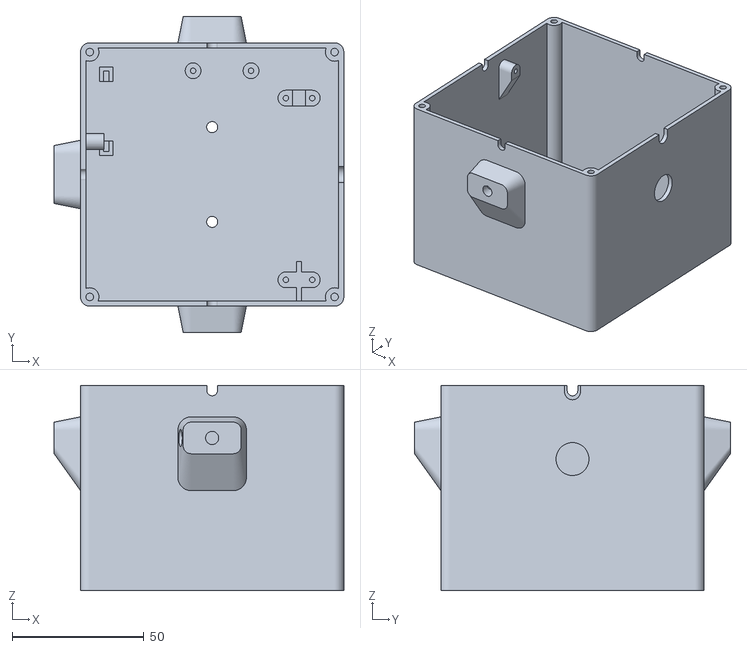
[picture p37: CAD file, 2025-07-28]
src/assets/3d-print/Case.stl
110.0 x 120.0 x 78.0

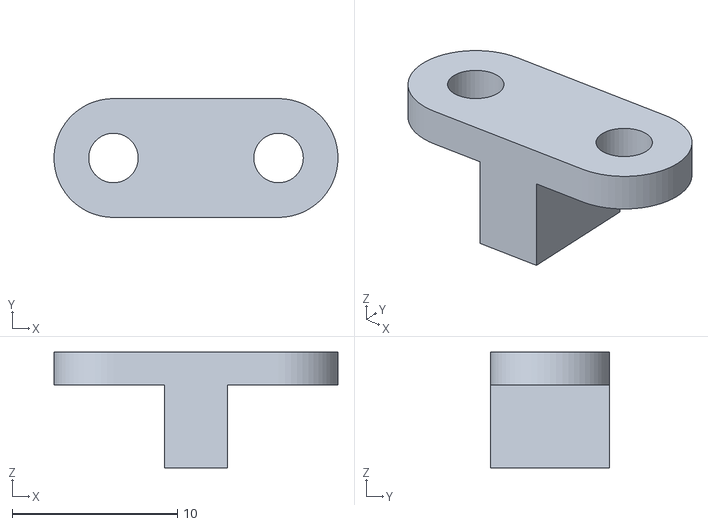
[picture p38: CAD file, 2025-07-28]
src/assets/3d-print/CableLocker.stl
17.2 x 7.20 x 7.00

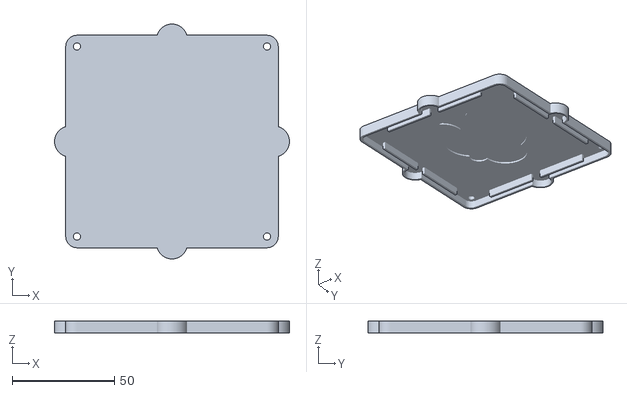
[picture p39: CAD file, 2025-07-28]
src/assets/3d-print/Lid.stl
115.0 x 115.0 x 6.00

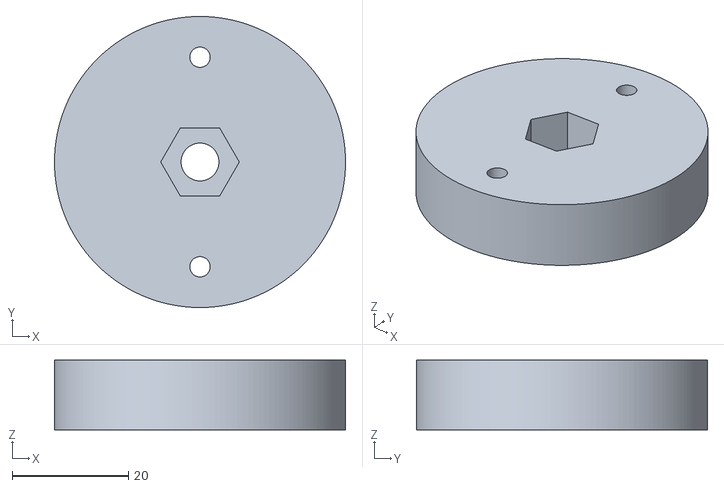
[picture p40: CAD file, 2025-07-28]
src/assets/3d-print/CameraTripodAdapter.stl
50.0 x 50.0 x 12.0

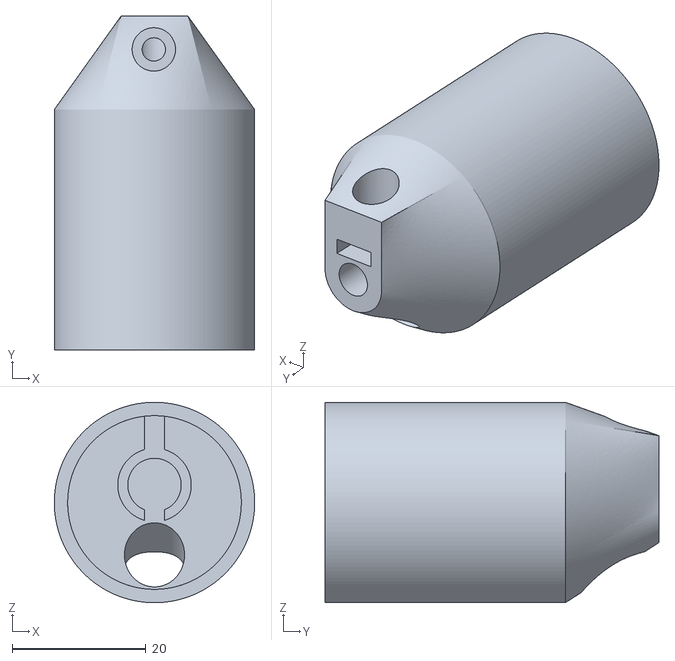
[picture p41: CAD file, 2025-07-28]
src/assets/3d-print/MicHolder_Lavalier.stl
30.0 x 50.0 x 30.0

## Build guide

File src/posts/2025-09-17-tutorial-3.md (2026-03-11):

---
title: Phase 3 - A DIY Solar-Powered Audio Streamer that Can Record Samples at Solar Times
date: 2025-09-17T10:00:00.000Z
excerpt: In this tutorial, I explain how to build the exact same solar-powered audio streamers we use in the forest.
permalink: /streamers/tutorial-3/
author: luigi-marino
draft: false
seo:
  title:
  description:
  image: /2025/07/all.jpg
images: # relative to /src/assets/images/
  feature: /2025/07/all.jpg
  thumb: /2025/07/all.jpg
  align: # object-center (default) - other options at https://tailwindcss.com/docs/object-position
  height: h-auto # optional. Default = h-48 md:h-1/3
tags:
  - acoustic-ecology
  - development  
  - diy-streamer
  - do-it-yourself
  - locus-sonus
  - raspberry-pi
  - soundscapes
  - streamers
  - tutorials
---

<!-- ![cover](/assets/images/2025/07/all.jpg) -->

## About this Tutorial

In this tutorial, I explain how to build the exact same solar-powered audio streamers we use in the forest.

Getting to the final version was a bumpy ride, so this guide offers more of a behind-the-scenes look at the challenges I faced, how I solved them, technical insights into the code, and real-world solar power data to ensure continuous operation.

But don’t worry! If you just want to get started quickly, there’s a more direct how-to guide: first, check the [**shopping list**](#shopping-list) then follow the instructions in the [**README file in our repository**](https://github.com/sensingtheforest/audio-streamer). If something doesn’t work or you’re not sure what’s going on, come back here for detailed explanations and tips.  

As everyone seems to focus on large AI models that require supercomputers accessible only to a few, this project goes in the opposite direction — using simple tech, guided by clever ideas, to solve specific problems while embracing **limitations**. For example, if a technology performs better but isn’t readily available, or might discourage a curious DIYer from experimenting, I either avoid it or suggest a more accessible alternative, as long as the alternative can still solve the problem effectively. When I read online that promising solutions like bioplastics aren’t recommended for outdoor use compared to petroleum-based plastics, I take that as a challenge to find ways to make them work. And more often than not, the solutions are there, if you look for them!

Some of the problems tackled here — which also double as stand-alone tutorials — include:

* **Nailing solar power requirements for Raspberry Pi projects.** And yes, solar works even in the UK *if* you meet the right requirements. Blanket statements like “solar doesn’t work in the UK” aren’t helpful. Through field testing (and only field testing), you'll get to what actually works.
* **Scheduling events based on solar time instead of standard clock time.** We used this to capture the dawn chorus of birds, but the same script can automate anything from turning on a terrarium light at sunrise to watering plants at sunset.
* **Updating and checking your remote Raspberry Pi with a 4g Dongle without relying on paid remote access services.**
* **Answering the question: can you trust 3D printed PLA parts for outdoor use?** Spoiler alert: the answer isn’t “no.”
* **Assessing the performance of ultra-cheap MEMS microphones as an alternative to electret mics in DIY projects where audio quality matters.** MEMS connect directly to the Raspberry Pi GPIO and don’t require a separate audio interface.

<br />

---

## Contents

- [Features](#features)
- [Acknowledgements and Origins](#acknowledgements-and-origins)
- [Shopping List](#shopping-list)
- [Wiring](#wiring)
- [3d Printed Parts](#3d-printed-parts)
- [Notes about the Microphones](#notes-about-the-microphones)
- [Overview of the Code Architecture](#overview-of-the-code-architecture)
- [The Safety Measures](#the-safety-measures)
- [How to Control the RPi from Your Home with a 4G Dongle — A real HACK!](#how-to-control-the-rpi-from-your-home-with-a-4g-dongle--a-real-hack)
- [Using a Smartphone Hotspot to Connect and Program the Raspberry Pi](#using-a-smartphone-hotspot-to-connect-and-program-the-raspberry-pi)
- [Automating tasks at astral time — Birds don’t sing at office hours...](#solar-crontab--birds-dont-sing-at-office-hours)
- [The Simplest Battery Sensor: ADS1115 breakout with voltage divider](#the-simplest-battery-sensor-ads1115-breakout-with-voltage-divider)
- [Getting The Solar Panel Setup Right](#getting-the-solar-panel-setup-right)
- [Best of Nature-Induced Tech Failure](#best-of-nature-induced-tech-failure)

<br />

---

## Features 

The streamer has the following features:

* Streams 24/7 stereo audio over the Internet
* Can automate recordings based on solar times (birds don't wear watches!)
* Built with DIYers in mind: Raspberry Pi, open-source code, 3D printing, and affordable, accessible materials
* Small and portable
* Stable and weather-resistant — it can run for months in harsh environments with no maintenance
* Uses the most eco-friendly materials we could reasonably find
* Fully solar-powered
* Remote monitoring and troubleshooting via 4G dongle (includes software updates, shell access, etc.)
* Local access via smartphone hotspot
* Range of audio qualities — suitable for curious DIYers looking for budget solutions, or audiophiles working with dedicated interfaces.

Everything shared here has been field-tested. Our streamers have worked for months, running on solar power even during UK winters, withstanding rain and snow. In their final version, they required minimal maintenance — and I'd say almost none if it weren’t for Storm Darragh, which briefly turned the solar panel into a sail before we tied everything to heavy logs...

<br />

---

## Acknowledgements and Origins 

Thanks to George Xenakis and Michael Bell from Forest Research for their practical, experience-based suggestions, which consistently proved accurate and saved us a great deal of trial and error. Thanks to Nick Wardlaw, Danielle Grimsey, Max Gravestock, and Jack Diprose at Forestry England for guiding us through the forest and supporting us at every step of the deployment.

Also, huge credit to the amazing [Locusonus project](https://locusonus.org/vitae/index.php?page=Locustream.en) (active since 2006), and their [streambox tutorial](https://locusonus.org/streambox/) — both of which were invaluable starting points.

That said, our 2024 project had different needs, and in the end, it evolved significantly from the original. Here's how it differs:

**Key Differences from the Streambox**
* Uses standard Raspberry Pi OS instead of Arch Linux
* No need to give remote access to anyone
* No pre-built OS image: we use a modular approach based on the latest RPi OS + online installers
* Built-in safety checks for remote deployment — automatic issue resolution
* New features:
  * Solar time-based automation
  * Remote code updates and shell access via 4G dongle

<br />

---

## Before you start

Make sure you understand the risks of leaving a 12V battery unattended in the field. I’ll repeat it throughout, but it’s worth saying clearly up front:
**Always use a fuse like shown in the wiring section, and thoroughly test your enclosure under both water and direct sunlight.**

**Don’t assume that in 2025 all remote areas have reliable network coverage.**
Alice Holt is a great example. Even in a well-visited, family-friendly forest managed by Forestry England, Anna and I spent a lot of time walking around with SIM cards from four different providers — and still found surprisingly few spots where even one offered a solid signal for our streamer to work.

<br />

---

## Shopping list 

<br />

#### Core Components

* [ ] Raspberry Pi Zero 2W
* [ ] Micro SD card (any size, we used 256GB but calculate storage needs based on recording time)
* [ ] 2 x Windshield (this 3D-printed holder fits the shield for Shure SM57 and mics with similar diameter)
* [ ] **Stereo Audio Input Options we tested**:

  * [ ] 2 × MEMS microphones with breakout (no audio interface needed, extremely cheap but low quality)
    **OR**
  * [ ] RØDE AI-Micro + 2 × Lavalier GO (or other lavalier mics)

<br />

#### Solar Power Setup

* [ ] Weather-resistant enclosure (we used a 24-litre Strata storage box made of recycled plastic)
* [ ] Battery Charge Controller with 5V USB Output
* [ ] 5A Fuse
* [ ] Fuse case

* [ ] Winter (December–January)
  * [ ] 4 × 120W solar panels (we used Eco-Worthy)
  * [ ] 120Ah 12V caravan battery

* [ ] Autumn & Spring
  * [ ] 2 × 120W solar panels
  * [ ] Any standard 12V car battery

* [ ] Summer
  * [ ] 1 × 100W solar panel
  * [ ] 7Ah 12V battery

> **Note**: These configurations worked for our specific conditions, and they are on the safe side. Solar requirements vary enormously based on region, sunlight exposure, and shading. For detailed explanation, refer to the relevant section in the guide.

<br />

#### Streaming Without LAN

* [ ] 4G USB modem
* [ ] Data SIM card with a suitable monthly plan
* [ ] Audio streaming host (we used StreamUp, supports up to 320 kbps OGG/VORBIS)

<br />

#### Battery Monitoring (Optional but very useful to nail the solar power requirements)

* [ ] ADS1115 breakout board
* [ ] 1 × 100kΩ resistor
* [ ] 1 × 330kΩ resistor
* [ ] Small stripboard (with vertical layout preferred)

<br />

#### 3D-Printed Case (Optional)

* [ ] 3D printer (to print from our shared model files)
* [ ] 4mm decorative aluminium wire
* [ ] Micro USB input breakout
* [ ] 12mm round waterproof on/off switch
* [ ] 5 × #2 self-tapping pan head 5mm screws
* [ ] 4 × #4 self-tapping pan head 5mm screws
* [ ] 3 × M3 square nuts
* [ ] 3 × M3 pan head 10mm bolts

<br />

**The total cost of the shopping list will mostly depend on your online shopping skills!** The most expensive part of the setup is usually the solar panel system, especially if you want the streamer to run 24/7 during winter. The total cost will be much lower if you only plan to stream during the sunnier seasons. For reference, if your goal is year-round streaming with no battery swap, an EcoWorthy 390W + controller package is currently about £200 (we used 4 × 120W panels for extra safety, but 390W should be enough even in the toughest winter months), and a 120Ah campervan lead-acid battery costs a little over £100 — though prices change quickly. The same goes for the SIM plan and 4G modem, as both prices and available models fluctuate so often that listing a fixed cost wouldn’t make sense. In short, if you’re setting up a simple home LAN streamer, all you really need is a Raspberry Pi and an audio capture device. See the section on microphones for a £10 stereo solution or a higher-quality option, but keep in mind that most USB audio devices work fine on an RPi Zero 2W, so the choice ultimately depends on your needs. That said, if you want to go all the way with a fully solar-powered streamer, including a year of SIM coverage and decent audio quality, the overall cost will be more substantial.

<br />

---
<br />
<br />
<br />

## Wiring 

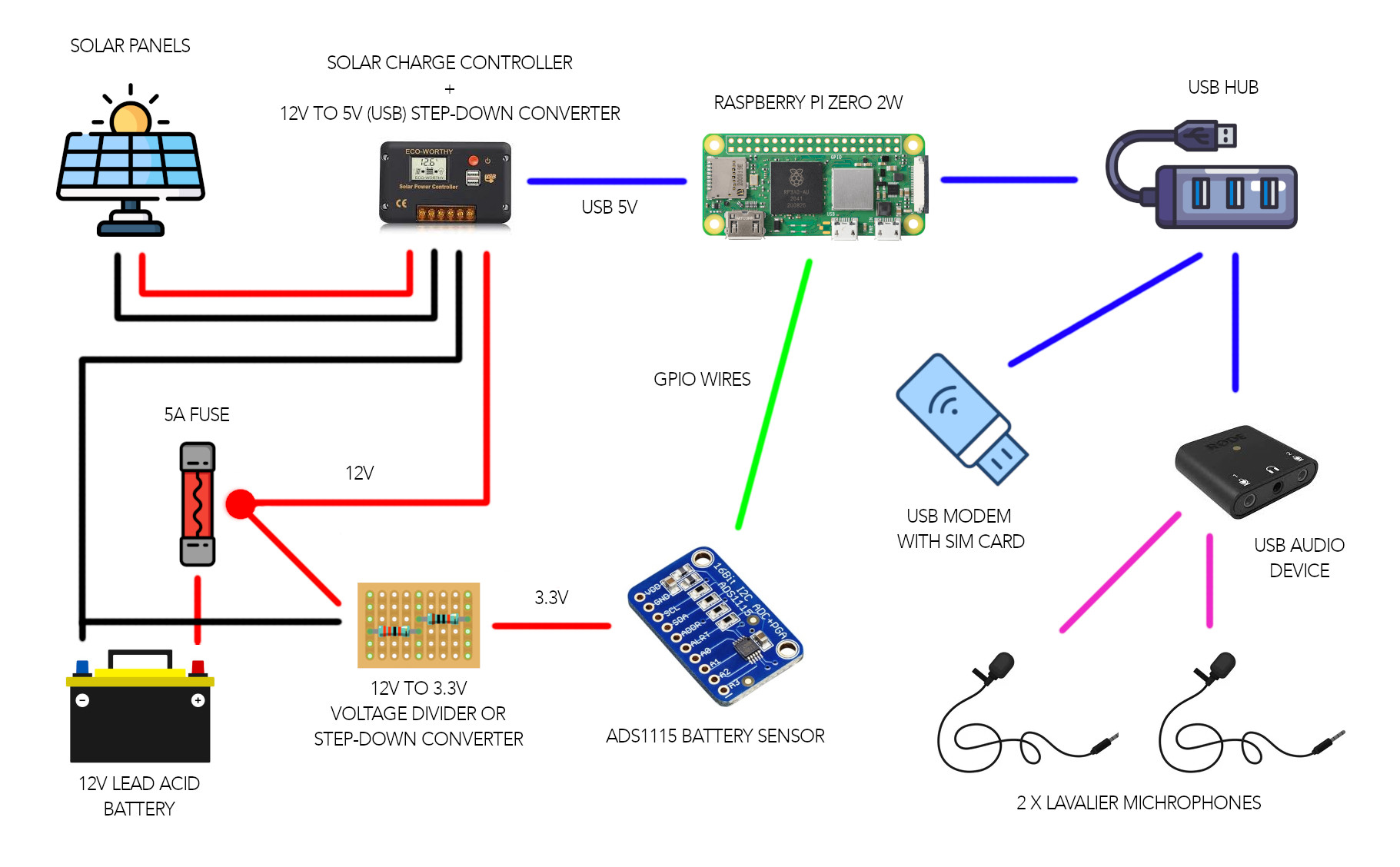
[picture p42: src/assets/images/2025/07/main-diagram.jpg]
wiring-diagram


The car battery, fuse, and charge controller go inside a box to protect them from the rain. **Always consider whether children are around!** If there’s any chance someone might touch the terminals, the box needs to be locked.

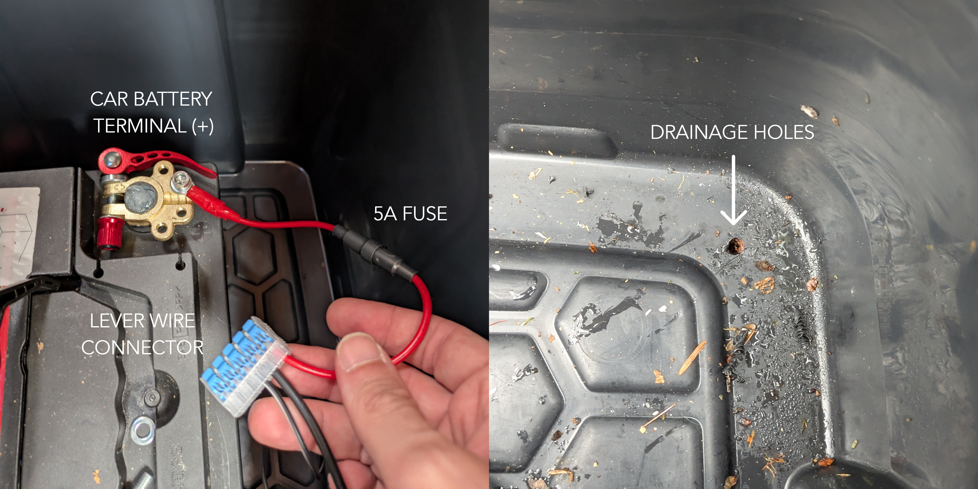
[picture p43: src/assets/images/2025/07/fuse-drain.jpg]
fuse


In the image on the left, you can see how I connected the fuse: it’s the first thing on the positive terminal of the battery. This way, if a short circuit happens anywhere else in the system, the fuse will blow. After the fuse, there’s a handy lever connector to plug and unplug all the parts that need 12V. In our setup, we send the 12V to the charge controller, which converts it to 5V for the USB powering the RPi. We also send the 12V to the voltage divider (or another step-down converter), which steps it down to 3.3V so the battery sensor can read it. (The digital pins expect a voltage between 0 and 3.3V.)

Drill drainage holes at the bottom of the box, just in case something goes very wrong and water gets inside. If the bettery will be out there for a long time, you can cover the terminals with dielectric grease: it will help prevent corrosion and, being waterproof and non-conductive, add another layer of safety.

For the assembly of the actual streamer with the microphones and the battery sensor, see the following sections.<br />
Once the current is stepped down to USB (5V), it’s much less dangerous to people and less critical if you make mistakes, so feel free to try stuff out! Though it can still damage electronics, the risk of injury or fire comes from mishandling the car battery. That said, I probably don’t need to remind you that most cars have flooded-acid batteries under the hood, and hopefully you don’t see many cars spontaneously catching fire… though their engine bays aren’t exactly waterproof either.

<br />

---

<br />
<br />
<br />

## 3D Printed Parts 

#### Downloads

FreeCAD:<br />
* [All](/assets/3d-print/streamer-ads1115-rpiVert-10cm.FCStd)<br />

Meshes:<br />
* [Case](/assets/3d-print/Case.stl)<br />
* [Lid](/assets/3d-print/Lid.stl)<br />
* [Cable Locker](/assets/3d-print/CableLocker.stl)<br />
* [Mic Holder (for Lavalier)](/assets/3d-print/MicHolder_Lavalier.stl)<br />
* [Mic Holder (for MEMS with round breakout)](/assets/3d-print/MicHolder_MEMS.stl)<br />
* [Camera Tripod Adapter](/assets/3d-print/CameraTripodAdapter.stl)<br />
* [Tree Shelf](/assets/3d-print/TreeShelf.stl)<br />
* [Modem Mushroom Case with antenna holes (for dongles with optional antennas)](/assets/3d-print/ModemCase_Mushroom.stl)<br />
* [Modem Flat Case (for SIM7600)](/assets/3d-print/Case.stl)

<br />

---

<table>
  <tr>
    <td align="center">
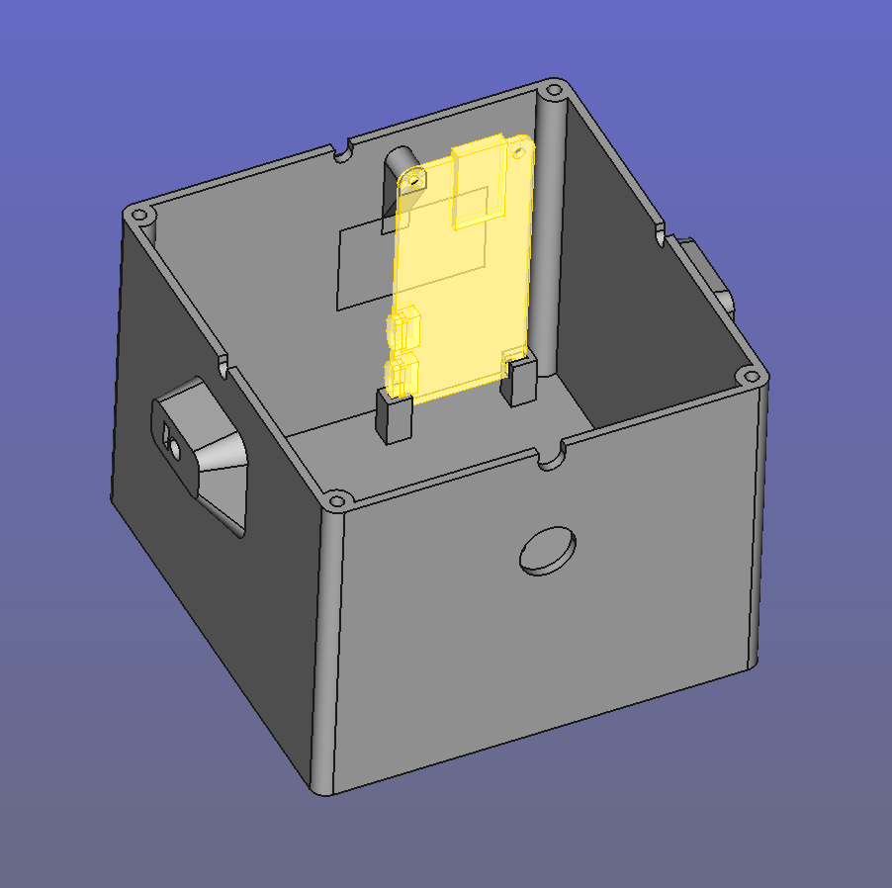
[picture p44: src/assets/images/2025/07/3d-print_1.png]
      <br />
      <strong>Lid (rain hat)</strong>
    </td>
    <td align="center">
      <img src="/assets/images/2025/07/3d-print_3.png" style="height:260px; width:100%” alt="mic"><br />
      <strong>Mic holder</strong>
    </td>
  </tr>
</table>

I assembled the parts, starting with the RPi, the battery sensor (see the corresponding section for build instructions), and the waterproof on/off switch. The case measures 10 × 10 × 8 cm, which provides enough space to fit a small USB hub and the AI-Micro.

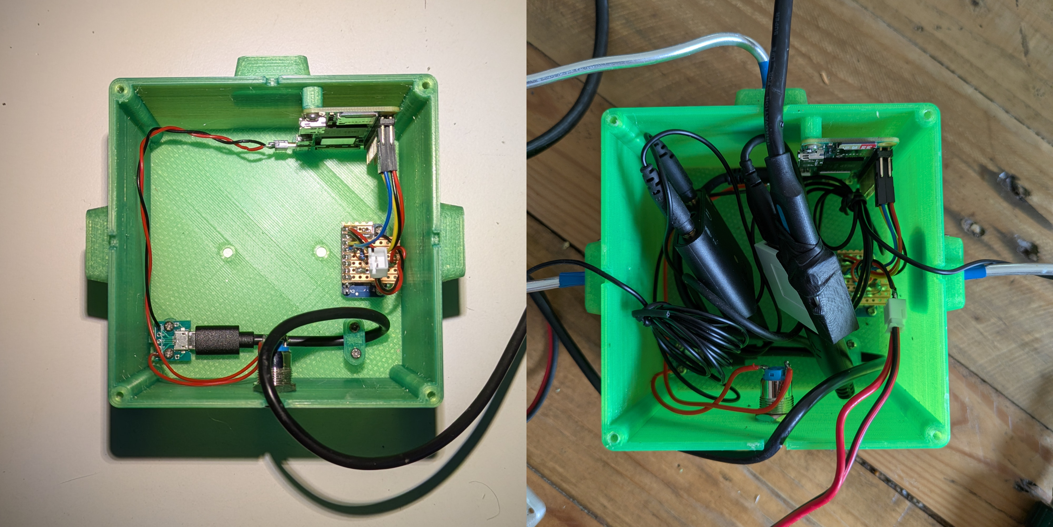
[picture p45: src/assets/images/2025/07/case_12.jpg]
case


**Note the vertical design for the RPi**. This way, I could collect the recordings by unscrewing only the lid and plugging the SD card directly into a Linux laptop. The root folder can be accessed from the normal file manager, just like an external flash drive. To download 40 GB of recordings, the scp remote protocol won’t help much, unless you can wait hours and hours.

All the parts that need connecting have a rectangular notch where you can slide in an M3 square nut. This holds the machine screw that locks the 4 mm aluminum wire in place. That way, you can move the parts into position, and the 4 mm wire alone is strong enough to keep them steady.
This is useful to control the stereo field of the microphones and the position of the modem - if the modem is too close to the RPi it causes interferences, more on this in the notes about microphones section. In the pictures below, I’m building the mic holder for lavaliers. Its diameter is designed to match the size of windshields for the common Shure SM57, so you can use that as a reference for the fit. 

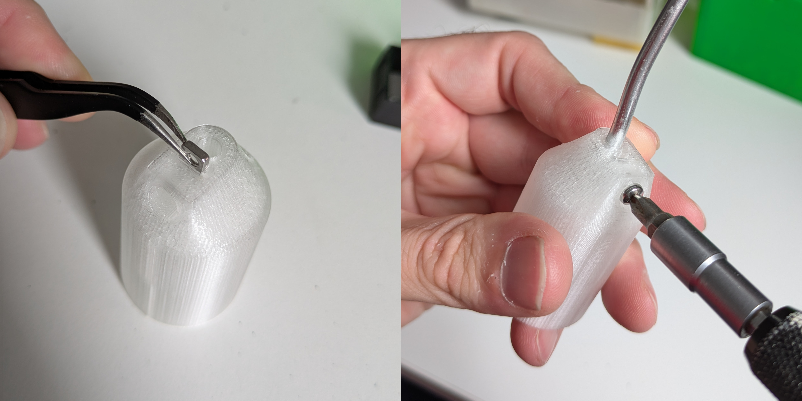
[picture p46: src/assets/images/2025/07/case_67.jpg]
case


All this parts were printed with standard PLA. And this leads to the question:
Will PLA survive a year of rain and sun in the forest?<br />
The internet: NO!<br />
ChatGPT: NO!<br />
My tests: well...

I didn’t head into the forest with the AI-Micro and the RØDE lavaliers right away. We started our tests with an RPi Zero and a couple of MEMS mics: if it all went horribly wrong, we’d have lost about £20.
A trick to make PLA waterproof and have cute mini boats floating in the bath is using beewax. So I coated the back of the lid with it. I coated the back only to keep the surface of the streamer nice and smooth. On top of that, I added rubber O-rings to the lid screws.

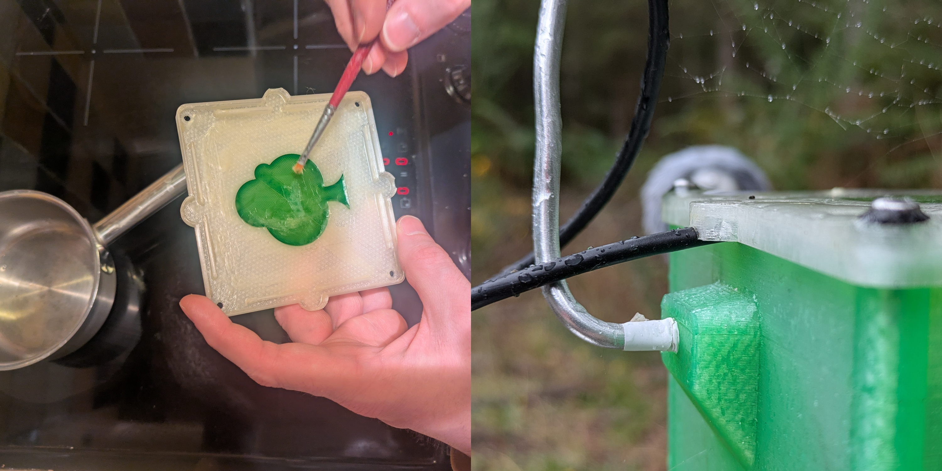
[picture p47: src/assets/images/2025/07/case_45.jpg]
case


I tested it under the shower to make sure the lid design would protect it from water coming from above. It passed.

In the right photo you can see a design detail: the lid has small semicircles with a downward-facing rim. They act like mini-umbrellas for the cable notches, and the rim presses down on the cables so raindrops can’t slide along them into the box (since, well, gravity wants the water to go from top to bottom).

Now, it’s true: PLA isn’t meant for outdoor use — UV light and moisture should eventually wear it down. But… the last version stayed out there from November to August, facing sun, rain, and snow, and not a single drop of water got through the lid. When we finally retired it, it didn’t look too beat up either:

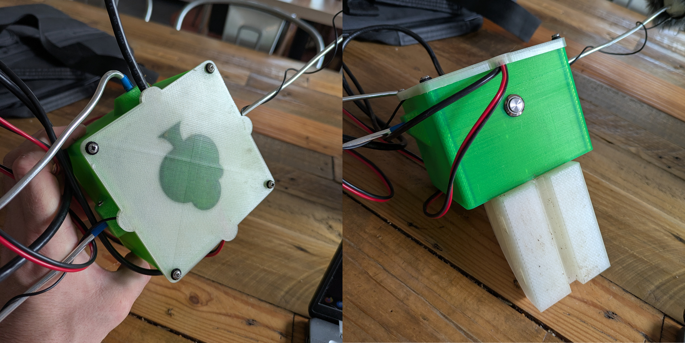
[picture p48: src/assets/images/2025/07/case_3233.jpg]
case


So, PLA turns out to be surprisingly resistant.
There are valid concerns about calling bioplastics like PLA eco-friendly—both because of the environmental costs of growing corn for feedstock and because industrial composting facilities are still rare. Under typical landfill conditions, PLA degrades very slowly, but in the right industrial facility it can break down within a few months, which is far better than petroleum-based plastics. In my area, companies like Vegware seem to be moving in the right direction by expanding the composting phase.

So while PLA is not a perfect solution, it seems to offer advantages over traditional plastics. My hope is that future research and infrastructure development will prove it to be more than just another case of greenwashing.

<br />

---
<br />
<br />
<br />

## Notes about the Microphones 

Choosing the right microphone turned out to be quite tricky. Since the equipment would be left unsupervised in a forest, often near a path, starting with high-end gear wasn’t an option.

A common solution online involved using Pi audio HATs with electret microphones, but these HATs tend to go out of production quickly. I wanted something that wouldn’t require rewriting code or adapting to new hardware every few months — so I ruled that out.

**USB microphones** were the next option. Most of the ones I tested were electret-based with onboard ADCs and worked plug-and-play on the Pi (see the first tutorial). But they’re typically mono. Using two with a USB hub might work, but you also need to power a 4G modem from the same hub — all running on battery. More importantly, I wanted flexible mic placement to control the stereo image, and USB mics in their housings make that harder. Bare capsules are easier to mount, protect from rain, and fit into custom 3D-printed enclosures.

**MEMS microphones** offered a lot of advantages:

* No need for an external audio interface or Pi HAT. ADC is onboard the coin-sized breakout.
* Most have 32-bit resolution.
* Extremely low current draw.
* Connect directly to the GPIO.
* Dirt cheap — you can get two (for stereo) for under £5.

For initial tests, especially with an untested DIY waterproof enclosure and uncertain site security, MEMS seemed like the perfect option.

However, their low current draw made them **very sensitive to interference**. 

After solving the interference issues, the quality was acceptable when sounds were relatively loud. But in the forest, silence is common, and at night or during quiet periods, the background noise (digital and noticeable) became an issue.

I then tested a very small audio interface designed for lavalier mics — compact enough to fit in an enclosure meant to go conmfortably up a tree. Few models offer dual input, but the **RØDE AI-Micro** with two **Lavalier GO** mics did the job. The improvement in interference was significant. The modem could sit much closer without problems, and even with the included 1.5 m unbalanced cables coiled up inside the box (right next to the battery wiring!), there was no noticeable interference — surprisingly stable for an unbalanced setup.

Setting up these USB devices is much easier than working with MEMS or Pi HATs. By following the instructions in the README file, you should have them up and running quickly.

> **Note:** The Rode AI-Micro comes — strangely — set to mix the left and right channels into mono by default. If you're using it, make sure to reconfigure it with the provided software, otherwise, you won't get separate left and right channels. This has to be done from a non-Linux machine.

The lavaliers with the AI-Micro is the final audio setup I used to record all the audio files you can hear on our Free Sound database, but only **from March onward**, when I switched from MEMS to the Lavaliers on both streamers.

<br />

---

#### *MEMS michrophones - Gradus ad Parnassum* (or maybe just a slightly less ambitious destination…)

MEMS microphones seem to be here to stay — and they might just become the go-to alternative to the ever-present electret mics for DIY projects. So here’s a bit of experimentation.
No sonograph allowed! Dear DIYer: if I say *“the audio here isn’t good”* but it sounds fine to you, you can skip the suggested improvements.

MEMS posed more problems than advertised.

**Step 1: just make it work.**

For the wiring, there is plenty of info online. [This project](https://makersportal.com/shop/i2s-mems-microphone-for-raspberry-pi-inmp441?srsltid=AfmBOoqB_DKFbKob098QTqIUZ4KEqHDwAs-WXdSmoxllFCNxPV8H_8t5) used exactly the MEMS breakout I found in stereo configuration, and the pins on Raspberry Pi zero 2W are the same.

You'll need to solder the headers and probably have a crimper for the connections. Initially, just use whatever cables you have.

Here’s what a MEMS mic can sound like if you:

* mismatch the bit resolution,
* don’t shield the cables, and
* use cables that are too long.

[▶️ Sound of MEMS with bit mismatch and unshielded cables, mono](https://raw.githubusercontent.com/sensingtheforest/sensingtheforest.github.io/main/src/assets/audio/1_mems_mono_16bit_shield-not-grounded.wav)

Keep in mind that these recordings were made in quiet settings, and the volume is relatively high to make details more audible.
But I promise, I’m not recording a synth with a random LFO — what sounds like a vintage oscillator is pure interference picked up by the unshielded cables in a noisy RF environment! Listening to nighttime forest sounds with this setup would be an unpleasant experience...

**Step 2: let’s get the cable length and shielding right.**

Now you’ll almost certainly need to deal with the shield, and 5-core shielded cables aren’t exactly common. You should be able to find them online, or you can make your own DIY shield.

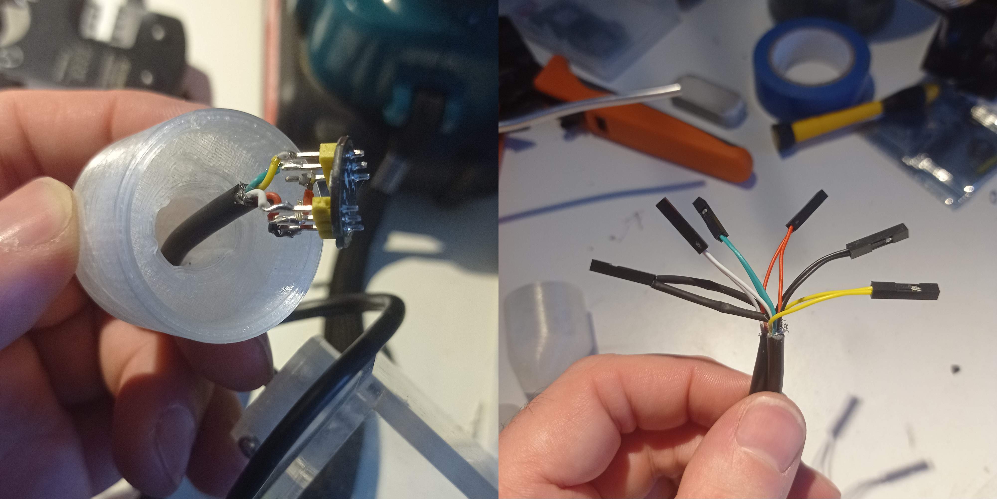
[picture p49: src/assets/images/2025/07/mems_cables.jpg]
mems-cables


On the left is a single mic, which I secure to the 3D-printed socket with hot glue. On the right are the two ends of the left and right mics, twisted together and crimped with the same connector. If you’re thinking in terms of analog audio, this might seem counterintuitive, but this is digital. Yes, L and R share some joined cables, yet you’ll still get separate channels on the Raspberry Pi — as long as you solder the R channel control pin to Vdd and the L channel control pin to ground. You can do this directly on the MEMS breakout board by connecting the Vdd pin to the control pin on one microphone, and ground to the control pin on the other.

The bit resolution is still mismatched, but the cables are now shielded — with the shield connected only on the Raspberry Pi side, tied to ground along with the cable ground.

[▶️ Sound of MEMS with bit mismatch and 50cm shielded cables, mono](https://raw.githubusercontent.com/sensingtheforest/sensingtheforest.github.io/main/src/assets/audio/2_mems_mono_16bit_shilded_medium-cable.wav)

The "synth" is quiter but still noticeably there. Cables are probably too long. Let's cut them from 50cm to about 15cm.

[▶️ Sound of MEMS with bit mismatch and 15cm shielded cables, mono](https://raw.githubusercontent.com/sensingtheforest/sensingtheforest.github.io/main/src/assets/audio/3_mems_mono_16bit_shielded_short-cable.wav)

Now, the “synth” is almost gone. Not perfect, but a major improvement. 

>**Note:**  There's no fixed rule for cable length. It depends entirely on the strength of RFI (radio frequency interference) in your environment. If you place the setup near a power line or a strong light source, it might not work at all. But in a low-interference area, a 1-meter cable might be just fine.

**Step 3: Can a bit-depth mismatch really cause that much trouble?**

My bit depth was 16-bit (S16\_LE). That’s wrong for most MEMS mics, which are typically 32-bit (S32\_LE).
This is the relevant part of the ALSA config file (`/etc/asound.conf`) 

```
pcm.mic_hw {
    type hw
    card sndrpii2scard
    channels 2
    format S16_LE   #16-bit is usually wrong for MEMS
}
```

[▶️ Sound of MEMS with bit depth mismatch, shielded and short cables, stereo](https://raw.githubusercontent.com/sensingtheforest/sensingtheforest.github.io/main/src/assets/audio/4_mems_stereo_16bit-instead-of-32_short-cable.wav)

Fixing the bit mismatch in the ALSA config file improved things a lot.

```
pcm.mic_hw {
    type hw
    card sndrpii2scard
    channels 2
    format S32_LE
}
```

[▶️ Sound of MEMS with correct bit depth, shielded and short cables, stereo](https://raw.githubusercontent.com/sensingtheforest/sensingtheforest.github.io/main/src/assets/audio/5_mems_stereo_32-bit-as-intended_short-cable.wav)

These recordings are from a morning in Bristol, and yes, we have a lot of seagulls here.
I expected it to reduce background noise — no surprises there — but it also helped significantly with interference when I moved everything to the forest, which I hadn’t anticipated, at least not to that extent. 

ALSA can be a bit unforgiving. If you don’t know the exact bit format of your device (not just the depth, but the label), it’s a real problem. Unfortunately, to figure it out for sure, you’ll probably need tools that come with PipeWire. That's what I used to discover that the AI-Micro works with 24-bit audio, 3 bytes per sample, Little Endian (S24_3LE). But if you’d rather avoid installing all that, a few educated guesses usually work. Start by trying `S32_LE`, then `S24_LE`.

**Step 4: The mic sounds decent, time to plug in the modem and head to the forest? Not so fast...**

You plug in the modem — and you hear a nasty glitch. You might think the mic’s broken. It’s not. That sound is **modem interference**, especially if you're trying to place it inside the same box as the MEMS mic and audio cables.

[▶️ Sound of MEMS next to the modem, stereo](https://raw.githubusercontent.com/sensingtheforest/sensingtheforest.github.io/main/src/assets/audio/6_mems_mono_16bit_near-modem.wav)

That’s the reason I built a separate modem case, connected by an aluminium wire — to isolate it from the audio path.

Move the modem farther away, and the glitch starts to fade:

[▶️ Sound of MEMS 30cm away from the modem, stereo](https://raw.githubusercontent.com/sensingtheforest/sensingtheforest.github.io/main/src/assets/audio/7_mems_mono_16bit_far-modem.wav)

And with proper shielding and enough distance, we’re back to where we started before plugging in the meodem.

<br />

---

**Circuit corrosion is real in the forest**

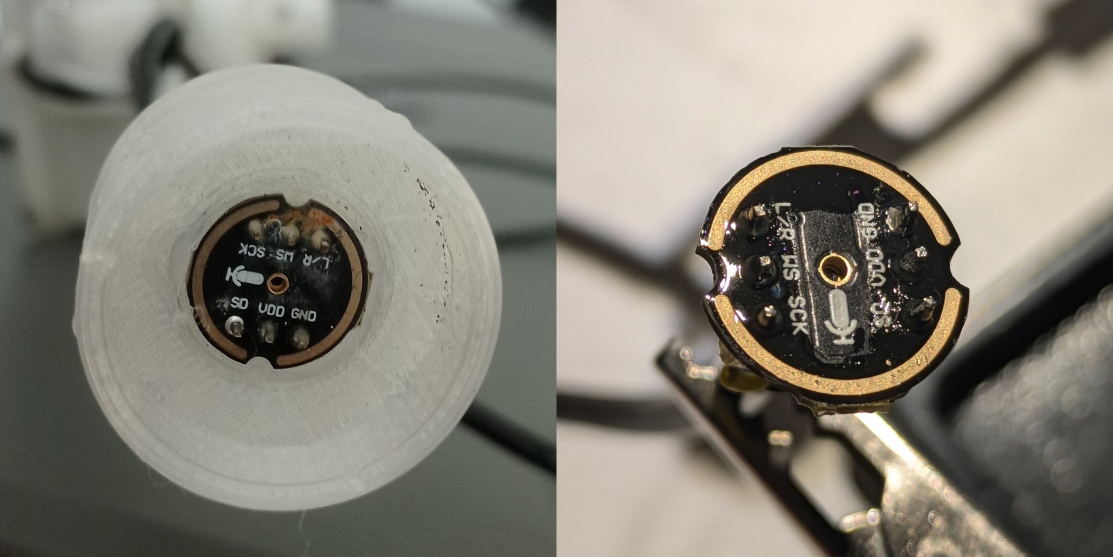
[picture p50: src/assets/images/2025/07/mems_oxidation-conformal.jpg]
mems-oxidation


On the left pic, you can see what happened to the exposed circuits after just a few weeks without protection.<br />
On the right, the fix: **applying acrylic conformal coating with a tiny brush solves the issue** — just make sure not to cover the mic hole!

In the rainy season, corrosion progresses faster, but it always starts gradually. Listen to the left channel below: the clicks aren’t rain; compare them to the right channel. This recording was made on September 23.

[▶️ Sound of MEMS with beginnings of corrosion on the L channel](https://raw.githubusercontent.com/sensingtheforest/sensingtheforest.github.io/main/src/assets/audio/8_corrosion-start.wav)

And yes, when advanced corrosion causes full short circuits, it can sound a lot closer to a Merzbow performance than to an idyllic forest soundscape! This is how it sounded on September 27, after four more humid days—volume reduced by 12 dB to spare your ears...

[▶️ Sound of MEMS with advanced corrosion on the L channel](https://raw.githubusercontent.com/sensingtheforest/sensingtheforest.github.io/main/src/assets/audio/9_corrosion-full.wav)

<br />

---
<br />
<br />
<br />

## Overview of the Code Architecture 

Most of the code is written in Bash, with Python scripts handling more time-sensitive tasks like reading the battery sensor and syncing with solar time.
System functions and global variables are defined in the `common.sh` script. <br />
**`common.sh` also acts as the main user configuration file. Many parameters of the streamer can be adjusted there, and each option is commented directly in the file.**

For audio streaming, I used Darkice, like Locusonus and many other similar projects online.

For full details, the code is available in our [GitHub repository](https://github.com/sensingtheforest/audio-streamer), and it's (hopefully!) well-commented. But here's a quick overview of the core structure of the streaming component:

```bash
boot.sh -> opens a detached screen session that runs stream.sh
   └── stream.sh -> runs monitor_stream() (a main while loop)
         └── monitor_stream() -> checks if darkice is running
               └── If not, starts darkice via start_darkice()
```

<br />

#### Monitoring Strategy

Instead of a simple `ps aux | grep darkice` process check (which often fails in edge cases), I implemented **live terminal parsing** of Darkice's output:

* If output ends with `SCHED_FIFO` → everything is fine, set streamer state to `1`
* If keywords like `reconnecting  0` or `TcpSocket` appear → set state to `0`, even if it later recovers (more about this later)

This state is stored in the `state.txt` file and read regularly to assess streaming health.

<br />

#### Why Live Parsing?

During field testing, I noticed Darkice could remain an active process but **fail silently** — e.g., not actually streaming due to a network dropout or crash. Live output parsing fixed that.

Now, if Darkice hits a known error state, it's killed and restarted. This even helps revive the remote streaming server — in our case StreamUp – likely because restarting triggers a fresh connection that resets the server-side socket state.

> **Note:** This method depends on specific terminal outputs from Darkice (set using `verbosity=6`). If future Darkice versions change these messages, the function will need to be updated.

<br />

---

<br />

#### Persistent Execution

* The main loop (`monitor_stream`) runs inside a **detached screen session** so it can operate independently of SSH connections.
* `boot.sh` sets everything in motion by launching the screen session at system startup using a **systemd** service.

See [**Tutorial One**](/streamers/tutorial-1) for more details on `screen`.

<br />

---
<br />
<br />
<br />

## The Safety Measures 

If you plan to leave the Streamer in a remote area, these are really (but REALLY) important. In the forest, literally everything that *could* go wrong, *did* go wrong. So here we tackle the software side of surviving the wilderness. Sure, if a tree falls on the Streamer, software won’t save you—but for many other adversities, we have error routines.

There are four levels of checks.

<br />

---

<br />

#### Level 1: `start_darkice()`

<br />

```bash
start_darkice() {
    if status_darkice; then
        log "start_darkice() - Darkice already running -> Kill and restart"
        kill_darkice
    fi
    log "start_darkice() - Start darkice with real-time output line check"
    sudo darkice -c "$PROJECT_FOLDER/darkice.cfg" -v 6 | while IFS= read -r darkice_line; do
        echo "$darkice_line" | tee -a "$LOG_FILE"
        if [[ "$darkice_line" == *"reconnecting  0"* || "$darkice_line" == *"TcpSocket"* || "$darkice_line" == *"No such device"* ]]; then
            set_darkice_state 0
        elif [[ "$darkice_line" == *"SCHED_FIFO"* ]]; then
            set_darkice_state 1
        fi
        sleep 0.1
    done
}
```

This function in `common.sh` watches Darkice’s terminal output in real time and flags issues we learned the hard way after a year of forest deployment. Around 80% of those issues were internet-related.

* `'reconnecting  0'` and `'TcpSocket'` usually meant the modem or network coverage had a meltdown.
* `'No such device'` was a fun one—it appeared when the AIMicro or Rode lav mic just decided not to exist anymore (after *months* of working fine, of course). It turned out the issue was failing USB cables or connections, which caused power shortages to the USB peripherals. Obviously, I didn’t get a simple on/off failure — that would’ve been easier to deal with. Instead, I had to troubleshoot increasingly intermittent and unreliable behaviour...

This function only **flags** problems. The actual fixing comes in later steps.

<br />

---

<br />

#### Level 2: `monitor_stream()`

This function runs every `DARKICE_MONITOR_INTERVAL` seconds (default: 60 — tweak it in `common.sh`). It checks the Darkice streaming state stored in `state.txt`.

If the flag is 0, it restarts Darkice. This solved a really annoying issue: when Darkice froze, sometimes the streaming server froze too. So even after Darkice came back, the server stayed unresponsive until we manually restarted it via CentovaCast.

Magically, restarting Darkice in these situations solved the server issue. Why? No idea. Maybe it reset the transmission protocol. Maybe it was just scared of getting rebooted again. But it worked.

<br />

---

<br />

#### Level 3: `monitor.sh`

This script is triggered by `crontab` every hour and takes a more “surgical” approach to problem-solving.

**Summary of what it does:**

* Checks if the Raspberry Pi has internet access.
* If not:

  * If using a dongle (not Wi-Fi), check and refresh the dongle's IP. If still down, reboot the dongle.
  * If using Wi-Fi, try reconnecting to known networks.
* If the internet comes back, restart the streaming session.
* Then verify if Darkice is *really* streaming (not just running). If stuck, kill the stream session and restart it.
* If recording is enabled, make sure `solar-crontab.py` is running. If not, restart it in a `screen` session.

<br />

---

<br />

#### Level 4: `nuclear-option.sh`

A bit of a dramatic name for a script that *just reboots the system*. But hey, when you're 5 hours away and stuck without logs, dramatic works.

Working in the forest was lovely—coding on a fallen tree while birds chirped around me—but driving back and forth every time the Pi decided to sulk wasn’t ideal.

The nuclear option was designed for those moments when nothing else works—especially if the modem crashes or your mobile provider surprises you with an unexpected IP change. The Raspberry Pi doesn’t always handle these disruptions gracefully, and sometimes a reboot is the only way to recover. Even before proper fallback routines kick in, a simple reboot can buy you another 12 hours of IP lease. And those 12 hours might be all you need to regain remote access and fix the issue.

In my case, those extra 12 hours after each reboot gave me time to remotely assign a permanent IP address to the modem, solving the lease expiry problem, thus sparing me a trip to the site, and, most importantly, avoiding any loss of recordings.

I set up this script to run once a day at 3 AM. Since rebooting sends logs via email and could cause more things to go wrong than the monitor script, I keep it rare.

<br />

---
<br />
<br />
<br />

## How to Control the RPi from Your Home with a 4G Dongle - A real HACK! 

When I finally got the 4G dongles to work, it sounded great... until I realized I couldn’t just SSH into the Raspberry Pi sitting deep in the woods. These dongles with SIM cards basically act like smartphones — and you wouldn’t want people SSH-ing into your phone either, right? Carriers make sure of that by throwing in things like CGNAT and constantly changing public IPs. Great for security, terrible for remote hacking (uh, I mean *maintenance*).

Sure, you could pay for services that give you a stable IP and remote access — just like they do for security cams — but where’s the fun in that? Hacks are free, fun, and they add that touch of cyberpunk.

<br />

---

<br />

#### Wait... Viruses Do This All the Time!

The idea is simple. Viruses often work by getting you to download a sketchy file that runs code on your machine. What if *we* are both the sender *and* the receiver — and we actually *trust* our code? Congratulations, you just reinvented the concept of **automatic updates**.

In a few words: we have a shared space (like an email inbox), the RPi checks it regularly, and if it finds something shiny (aka an email with a subject of your choice and with an attachment), it downloads and runs it.

<br />

---

<br />

#### The Simplest Possible Shared Repo: Email

Yes. Email. Literally Gmail.

To set this up:

* Enable IMAP on your Gmail account
* Write a Python script that checks for emails with a specific subject and grabs the attachments
* Tell the Pi to run that script on a schedule and execute the goodies it downloads

<br />

---

<br />

#### How to Enable IMAP on Gmail

1. Open Gmail, click the gear icon (top-right), then “See all settings”
2. Go to **Forwarding and POP/IMAP**
3. Under **IMAP Access**, select “Enable IMAP”, then click “Save Changes”

Done.

<br />

---

<br />

#### The Python Snippet That Does the Job

This little script checks your Gmail inbox, looks for emails with a certain subject from the past few days (tweak this with the var SEARCH_DAYS), and downloads any attachments into your Pi's project folder.
**Heads up:** Don’t forget to enable IMAP on your email and update the placeholders in the Email account credentials section of the code before running it!

```python
from pathlib import Path
import imaplib
import email
import os
from datetime import datetime, timedelta

# --- Email account credentials and script config (edit this section!) ---
IMAP_SERVER = "imap.gmail.com"
EMAIL_ACCOUNT = "your-email@gmail.com"
PASSWORD = "your-app-password"  # Use a Google app password, not your main account password
PROJECT_DIR = Path(__file__).resolve().parent
SEARCH_SUBJECT = "update code myProjectName"  # <-- Change to match your subject line
SEARCH_DAYS = 3  # Number of days to look back in the inbox
# ------------------------------------------------------------------------

print("______________UPDATE CODE")

# Calculate the date x days ago in IMAP format (DD-MM-YYYY)
date_x_days_ago = (datetime.now() - timedelta(days=SEARCH_DAYS)).strftime("%d-%b-%Y")

# Connect to email server
mail = imaplib.IMAP4_SSL(IMAP_SERVER)
mail.login(EMAIL_ACCOUNT, PASSWORD)
mail.select("inbox")

# Search for emails with the subject and date filter
search_criteria = f'(SINCE {date_x_days_ago} SUBJECT "{SEARCH_SUBJECT}")'
status, messages = mail.search(None, search_criteria)

email_ids = messages[0].split()
if not email_ids:
    print(f"No recent emails found with subject: {SEARCH_SUBJECT}")
else:
    latest_email_id = email_ids[-1]
    status, data = mail.fetch(latest_email_id, "(RFC822)")
    msg = email.message_from_bytes(data[0][1])

    print(f"From: {msg['From']}")
    print(f"Subject: {msg['Subject']}")
    print(f"Date: {msg['Date']}")

    # Loop through email parts to find attachments
    for part in msg.walk():
        if part.get_content_disposition() == "attachment":
            filename = part.get_filename()
            if filename:
                filepath = os.path.join(PROJECT_DIR, filename)
                with open(filepath, "wb") as f:
                    f.write(part.get_payload(decode=True))
                print(f"Saved attachment: {filepath}")

mail.logout()
print("DONE")
```

<br />

---

<br />

#### What If You Just Want to Run Shell Commands?

<br />

Great question. You’re not always uploading new scripts — sometimes you just want to run a `reboot`, or log the CPU temp, or sacrifice a process to the gods of uptime.

Here’s the plan: we download a shell script via email (same method as above), and run it if it exists. Since we’ve already automated the email checking, we don’t want to repeat the commands every time the cronjob kicks in.

So, here comes the little extra step that makes it all neat and modular.

This helper script `blank.sh` looks for a file called `commands-tray.sh` in the project folder — a sort of “meal tray” you send via email. It contains all the commands you want the RPi to execute.

The moment we run `blank.sh` and it finds a file called `commands-tray.sh` with the bash commands, it eagerly devours its contents (i.e., runs the commands), logs the output, and then throws the tray in the bin (i.e., deletes `commands-tray.sh`) so it doesn’t rerun the same stuff over and over—unless you forget to delete the email, in which case it will keep finding commands to execute.

```bash
source "$(dirname "$(realpath "${BASH_SOURCE[0]}")")"/common.sh
script_name=$(basename "${BASH_SOURCE[0]}")

commands_script="$PROJECT_FOLDER/commands-tray.sh"
temp_log=$(mktemp)

if [[ -f "$commands_script" && -s "$commands_script" ]]; then
    log "$script_name - Executing $commands_script..."
    log "$(cat $commands_script)"
    source "$commands_script" > >(tee -a "$temp_log") 2>&1
    log "$(cat "$temp_log")"
    log "$script_name - Execution completed. Deleting $commands_script..."
    sudo rm -f "$commands_script" && rm -f "$temp_log"
else
    log "$script_name - No commands to execute."
fi

if [[ -n "$reboot" && "$reboot" -eq 1 ]]; then
    log "$script_name - Rebooting now..."
    sudo reboot
fi
```

<br />

---

<br />

#### Automate blank.sh With Cron

<br />

We want the RPi to check its inbox regularly, so we set up a cronjob to download the attachments and run `blank.sh` a few seconds after:

```md
0 * * * * $HOME/audio-streamer/venv/bin/python $HOME/audio-streamer/update-code.py && sleep 10 && $HOME/audio-streamer/blank.sh
```

This runs every hour. If you're confident everything’s stable, once a day should be fine too.

<br />

---

That’s it. You’ve now got remote, wireless, email-powered code deployment and shell control for your Raspberry Pi in the middle of nowhere — no subscriptions, no exposed SSH ports, no nonsense. Just some hackery.

<br />

---

<br />

#### Remote Command Greatest Hits (Only the Ones That Actually Worked)

<br />

Here’s a little greatest hits mixtape of the remote commands I sent to the streamer by uploading `commands-tray.sh`. Only the ones that actually did something useful made it into this list.

> Reminder: `blank.sh` uses `source` to load `commands-tray.sh` (not a subshell), so all the global variables from `common.sh` are available in the current session.

- **Reboot**

This is the **only command with special syntax** because it gets executed **after** the script finishes.
**Don't** use `sudo reboot` here — otherwise, the script will halt before cleaning up temporary files or deleting itself.

```bash
reboot=1
```

From here on, just standard bash...

- **Send the Latest System Log**

You'll receive `sys.log` in your inbox the next time `blank.sh` runs.

```bash
$PROJECT_FOLDER/send-email.sh
```

- **Get the Current Configuration Files of the Streamer**

Send the key config files one by one.

```bash
$PROJECT_FOLDER/send-email.sh -a $PROJECT_FOLDER/darkice.cfg -s "STREAMER CONFIG: darkice.cfg"
$PROJECT_FOLDER/send-email.sh -a $PROJECT_FOLDER/update-code.py -s "STREAMER CONFIG: update-code.py"
$PROJECT_FOLDER/send-email.sh -a $PROJECT_FOLDER/solar-crontab.py -s "STREAMER CONFIG: solar-crontab.py"
$PROJECT_FOLDER/send-email.sh -a $PROJECT_FOLDER/common.sh -s "STREAMER CONFIG: common.sh"
$PROJECT_FOLDER/send-email.sh -a ~/.msmtprc -s "STREAMER CONFIG: msmtprc"
```

Or just send them all in one email — `send-email.sh` accepts multiple attachments.

```bash
$PROJECT_FOLDER/send-email.sh \
  -a $PROJECT_FOLDER/darkice.cfg \
  -a $PROJECT_FOLDER/common.sh \
  -a $PROJECT_FOLDER/update-code.py \
  -a $PROJECT_FOLDER/solar-crontab.py \
  -a ~/.msmtprc \
  -s "STREAMER CONFIG: Full config dump"
```

- **Add a new cronjob**

This command adds a new cron job to the end of the crontab. The job schedules recordings to run every hour from 11:00 AM to 5:00 PM. These entries won’t interfere with the solar-based cron jobs (see next section), even if they overlap, because `record.sh` will create a separate audio file for each run.

```bash
(crontab -l; echo "0 11-17 * * * $HOME/audio-streamer/record.sh") | crontab -
```

- **Update a cronjob**
  
Replace specific lines in your crontab with new ones.

Edit the remote update check to run every hour,
instead of every 4 hours as defined in the default cronjob.

```bash
crontab -l | sed 's|0 \*/4 \* \* \* \$HOME/audio-streamer/venv/bin/python \$HOME/audio-streamer/update-code.py|20 * * * * $HOME/audio-streamer/venv/bin/python $HOME/audio-streamer/update-code.py|' | crontab -
```

- **Amend a cronjob to use a new script**
```bash
crontab -l | sed 's|\$HOME/audio-streamer/email-log.sh|\$HOME/audio-streamer/send-email.sh|' | crontab -
```

- **Save your crontab contents to `sys.log` and send it**
```bash
crontab -l >> "$PROJECT_FOLDER/sys.log"
$PROJECT_FOLDER/send-email.sh
```

- **Log all audio files and email the list**
```bash
ls -1 "$PROJECT_FOLDER/audio" > "$PROJECT_FOLDER/rec.log"
$PROJECT_FOLDER/send-email.sh -a $PROJECT_FOLDER/rec.log -s "STREAMER DATA: Audio recordings log"
```

- **Uploaded a sys file and it's not working? Often, a just matter of permissions**
  
Check the `sys.log` for clues: it usually shows a "permission denied" error. To solve this, grant read permission (`+r`) to all users (`a`) to fix it and try sending it again via email:
```bash
sudo chmod a+r /etc/asound.conf
$PROJECT_FOLDER/send-email.sh -a /etc/asound.conf -s "STREAMER SOUNDSCAPE: Current asound.conf"
```

<br />

---
<br />
<br />
<br />

## Using a Smartphone Hotspot to Connect and Program the Raspberry Pi 

Sometimes (often initially) I had to debug and code the RPi in the forest, and I couldn’t wait an hour for the upload technique through email. It turns out that a smartphone hotspot and a couple of free apps were everything I needed.

<br />

#### 1. Apps, Setup, and Hotspot

1. Download *Net Analyzer* and *Termius* on your smartphone.
2. Make sure you wrote the correct SSID and password of your smartphone hotspot in the appropriate section of `common.sh`.
3. Enable the hotspot and power on the RPi.

<br />

---
<br />

#### 2. Find the RPi’s IP (Net Analyzer)

1. Connect your phone to its own hotspot.
2. Open *Net Analyzer* → run a LAN scan. (Tip: you may need to turn off your phone’s main Wi-Fi for the scan to succeed.)
3. Look for a device named *Raspberry Pi Foundation* (or similar).
4. Note the IP address (e.g., `192.168.43.101`).

<br />

---
<br />

#### 3. Connect via SSH (Termius)

1. Open *Termius*.
2. Add a *new host*:

   * Address: IP from Net Analyzer.
   * Username: your RPi username.
   * Password: your RPi password.
3. Save → Connect → You now have an SSH shell to the Pi.

<br />

---
<br />

#### Tips

1. Coding on a smartphone is a recipe for bugs, but not all smartphones let you connect a laptop and RPi to the hotspot and SSH from the laptop to the RPi. I tried it with a Google Pixel and it worked like a charm, but when students tried with their devices, most blocked this, especially iPhones. Programming directly from the smartphone is often the only solution unless you have a dedicated portable hotspot.

2. **More of a warning → Verify that the RPi auto-connects to your hotspot before heading into the field!**

<br />

---
<br />
<br />
<br />

## Solar Crontab — *Birds don’t sing at office hours!* 

The usual way to schedule things on Linux is with good old `crontab`. You pick an hour, a day, a month, and the job gets done. But nature doesn’t run on clocks — it runs on light.

When we set up our forest recorder, we really wanted to capture dawn choruses of the birds that starts just before sunrise and fades as the day begins. So syncing with the sun was a must.

That's where this script comes in: it triggers scripts or Python functions **based on solar events**, not man-made time. It's flexible too — I've used it to turn on terrarium lights, water a garden, and yes, start a remote recording session as soon as the birds start gossiping.

This version is cleaned up and doesn't depend on the audio streamer repo, so you can use it for any project.

<br />

---

<br />

#### How it works

<br />

* You define a **location** (lat/lon + timezone).
* You specify some **solar ratios**:
  `0` = sunrise, `1` = solar noon, `2` = sunset.
  You can get creative — e.g., `2.5` is halfway between sunset and the *next* sunrise (i.e., middle of the night).
* You assign a **command** (bash script or Python function) to each ratio.
* The script checks the solar events for *today*, waits until the next one, runs the command, and repeats forever like a tiny sun-worshipping daemon.

<br />

---

<br />

#### Python script and setup

<br />

```python
from pathlib import Path
import os
from datetime import datetime, timedelta
import time
import zoneinfo
from astral import LocationInfo
from astral.sun import sun

#################################################
# Edit your parameters here:

location = LocationInfo("Alice Holt Forest", "UK", "Europe/London", 51.1699307, -0.8371404)

# Solar ratios: 0 = sunrise, 1 = noon, 2 = sunset, 2.5 = night (between sunset and sunrise)
solar_ratios = [0.0, 1.0, 2.0, 2.5]

SCRIPT_DIR = Path(__file__).resolve().parent
commands = [""] * len(solar_ratios)

# Shell scripts or Python functions
commands[0] = os.path.join(SCRIPT_DIR, "record.sh")
commands[1] = os.path.join(SCRIPT_DIR, "record.sh")
commands[2] = os.path.join(SCRIPT_DIR, "record.sh")
commands[3] = os.path.join(SCRIPT_DIR, "record.sh")

# If you need to use Python functions instead of shell scripts,
# assign them without parentheses or arguments. You can mix bash and Python functions.
# commands[0] = myPythonFunction

#################################################

tz = zoneinfo.ZoneInfo(location.timezone)

def execute_command(command):
    if command is None or (isinstance(command, str) and command.strip() == ""):
        print("Nothing to run.")
        return

    if isinstance(command, str):
        os.system(command)
        print(f"Executed shell command: {command}")
    elif callable(command):
        try:
            command()
            print("Executed Python function.")
        except Exception as e:
            print(f"Error in Python function: {e}")
    else:
        print(f"Unsupported command type: {type(command)}")

def get_sun_times(location):
    today = datetime.now(tz).date()
    sun_times = sun(location.observer, date=today, tzinfo=tz)
    return sun_times["sunrise"], sun_times["sunset"], sun_times["noon"]

def datetime_to_timedelta(dt):
    return timedelta(hours=dt.hour, minutes=dt.minute, seconds=dt.second)

def calculate_intermediate_time(start, end, ratio):
    return start + (end - start) * ratio

def convert_ratios_to_times(ratios, sunrise, noon, sunset):
    sunrise_td = datetime_to_timedelta(sunrise)
    noon_td = datetime_to_timedelta(noon)
    sunset_td = datetime_to_timedelta(sunset)
    times = []

    for ratio in ratios:
        if ratio <= 1:
            td = calculate_intermediate_time(sunrise_td, noon_td, ratio)
        elif ratio <= 2:
            td = calculate_intermediate_time(noon_td, sunset_td, ratio - 1)
        else:
            td = calculate_intermediate_time(sunset_td, sunrise_td + timedelta(days=1), ratio - 2)
        times.append(datetime.combine(datetime.today(), datetime.min.time(), tz) + td)

    return times

def print_solar_times(ratios, times):
    print("Today's solar events:")
    for ratio, time in zip(ratios, times):
        print(f"  → Ratio {ratio}: {time.strftime('%H:%M:%S')}")

def calculate_delay(target_time):
    now = datetime.now(tz)
    delay = (target_time - now).total_seconds()
    return delay + 86400 if delay < 0 else delay

# Main loop
if __name__ == "__main__":
    print(f"Location: {location.name}, {location.region}")
    print(f"Lat: {location.latitude}, Lon: {location.longitude}")

    while True:
        sunrise, sunset, noon = get_sun_times(location)
        solar_times = convert_ratios_to_times(solar_ratios, sunrise, noon, sunset)
        print_solar_times(solar_ratios, solar_times)

        delays = [calculate_delay(t) for t in solar_times]
        next_idx = delays.index(min(delays))

        next_time = solar_times[next_idx]
        next_delay = delays[next_idx]
        next_ratio = solar_ratios[next_idx]
        next_command = commands[next_idx]

        print(f"Next event (ratio {next_ratio}) in {int(next_delay)} seconds at {next_time.strftime('%H:%M:%S')}")
        time.sleep(next_delay)

        execute_command(next_command)
        print("Waiting one minute to avoid double-triggers...\n")
        time.sleep(60)
```

<br />

---
<br />
<br />
<br />

## The Simplest Battery Sensor: ADS1115 breakout with voltage divider 

The battery sensor is incredibly useful for monitoring a solar-powered setup. This one is pretty basic, but it gets the job done. I used a common analog-to-digital converter (ADS1115) to read the battery voltage directly, and a simple voltage divider—just two resistors—to scale the 12 V down to 3.3 V (with some headroom), which the Raspberry Pi can safely read on one of its GPIO input pins. For the voltage divider I soldered a piece of breadboard with the conductive side up.

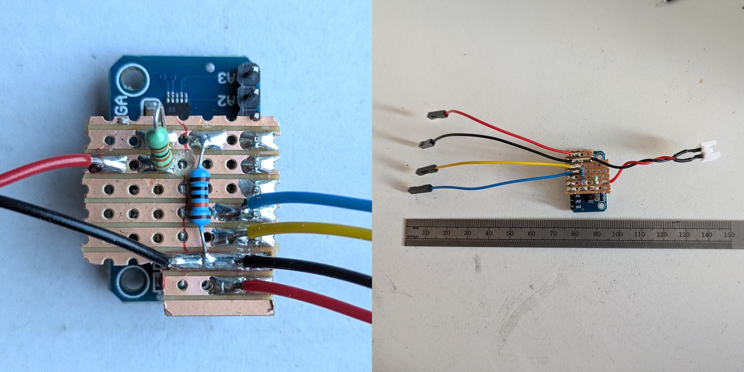
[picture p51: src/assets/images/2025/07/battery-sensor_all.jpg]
battery sensor


You should **definitely include a fuse** in this setup. If you leave it in a place with fire hazard, it's absolutely **mandatory** — but if you're using this specific voltage divider, the fuse isn’t just mandatory, it’s **non-negotiable**. You're connecting the **+ and – from a 12V battery directly onto a tiny breadboard**. A stray wire, a drop of water — that's all it takes to **short the rails**, and **car batteries can dump hundreds of amps in a flash**.

**Anything around 5A will do.** A cheap inline fuse could save your gear — or the entire site if you're not very careful.

In the picture, I soldered all the wires on the stripboard, so if I make mistakes, I don’t have to mess with the sensor itself. That part is left out in the diagram for clarity.

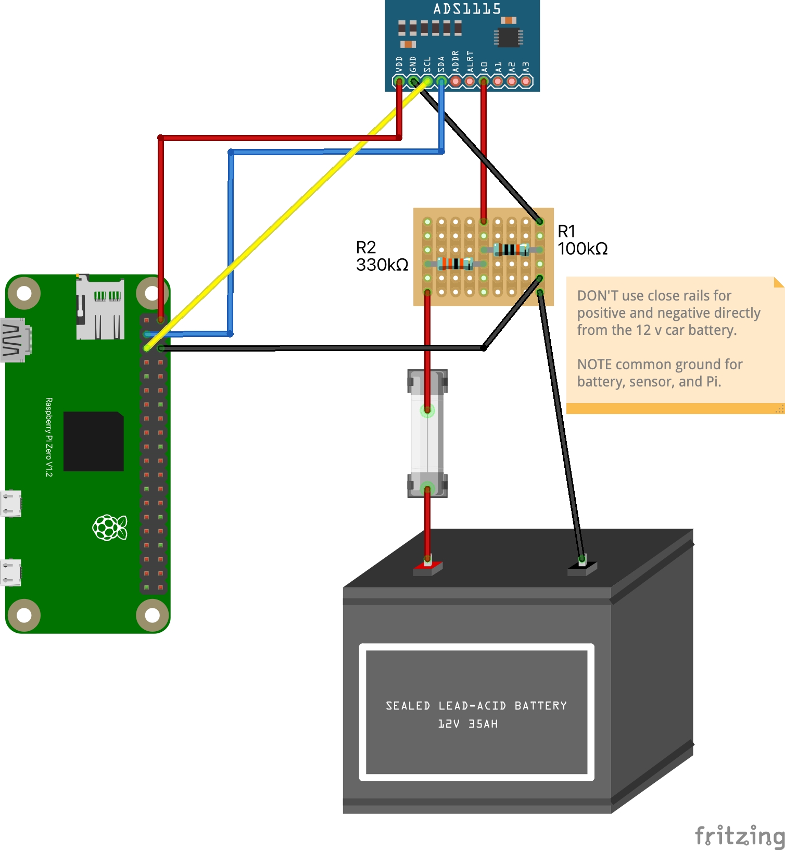
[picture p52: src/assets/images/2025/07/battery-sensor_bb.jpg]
battery sensor


Below there is the Python code used to read the battery voltage. Here, I removed the functions that log the values to the project log, so this code can be used separately if you're only interested in the battery sensor. But the original script I use with the streamer is in the repo.

The voltage divider can be built with many combinations of resistor values — but **if you change the resistors, you must also update the values in the code** so that the function can rescale the readings accordingly. (Yes, this is one of those cases where analog and digital meet in a very tangible and understandable way!)

Also, the sensor **needs calibration**. Here, I implemented the simplest possible method: comparing one reading from the sensor to a manual reading taken with a multimeter. You should do the same and change the values in the code to reflect your setup.
The correct way (as George at Forest Research reminds us) is to take several readings at different battery charge levels and use those to build a proper scaling function. But if you don’t need extreme precision, a single comparison point will usually do the job just fine.

```python
import time
import board
import busio
import adafruit_ads1x15.ads1115 as ADS
from adafruit_ads1x15.analog_in import AnalogIn

# Create I2C bus
i2c = busio.I2C(board.SCL, board.SDA)

# Create ADS1115 object
ads = ADS.ADS1115(i2c)

# Set the gain to handle voltages up to 4.096V (ADS1115 reference voltage)
ads.gain = 1  # Gain of 1 corresponds to ±4.096V range

# Select the input channel to read (e.g., A0)
channel = AnalogIn(ads, ADS.P0)

# Voltage divider parameters
R1 = 330000  # 330kΩ resistor
R2 = 100000  # 100kΩ resistor

# Divider factor
divider_ratio = R2 / (R1 + R2)  

# Measurments for calibration
sensor_voltage = 13.1
multimeter_voltage = 13.05

calibration_factor = multimeter_voltage / sensor_voltage

def read_battery_voltage():
    # Read raw ADC voltage
    adc_voltage = channel.voltage  # Voltage at the ADC pin (post-divider)
    # Calculate the actual battery voltage
    battery_voltage = (adc_voltage / divider_ratio) * calibration_factor
    return battery_voltage

# Dummy read. After boot, the first read is wrong.
channel.voltage
time.sleep(0.1)

if __name__ == "__main__":
    battery_voltage = read_battery_voltage()
    print(f"Battery Voltage: {battery_voltage:.2f} V")
```

If you're using our installer, all required libraries should already be included.

But if you're setting up only the battery sensor, you'll need to install a few Python libraries and run the script inside a **virtual environment**, as required by Python on Raspberry Pi OS *Bookworm* and newer.

```bash
sudo apt install -y python3-pip

# Create and activate the virtual environment
python3 -m venv venv
source venv/bin/activate

# Install required libraries inside the venv
pip install RPi.GPIO
pip install adafruit-blinka
pip install adafruit-circuitpython-ads1x15
```

Make sure to **run your script inside the activated venv** each time:

```bash
source venv/bin/activate
python your_script.py
```

To activate the venv and log the voltage automatically with `crontab` (e.g. every half hour), use this line instead:

```md
0,30 * * * * $HOME/audio-streamer/venv/bin/python $HOME/audio-streamer/battery.py
```

<br />

---
<br />
<br />
<br />

## Getting the Solar Panel Setup Right 

If there’s one thing no blog post, forum, or ChatGPT session could really help me solve without getting my hands dirty, it was figuring out the solar power requirements to keep a low-power streamer alive through a UK winter.

So here we go.

I started experimenting in June 2024. Between June and August, in an open field, *anything works*. A standard 80W or 100W panel plus a 12V 7AH battery is plenty to keep a Raspberry Pi running 24/7. Most of the panels you find online come with a basic controller, usually with at least one 5V USB output — just plug it into the Pi and you’re done.

One key detail: USB cables are the weak point, especially the junctions. Keep them short, avoid unnecessary splits or adapters, and protect any exposed joins with self-amalgamating tape. It really helps.

In our setup for Pete's installation, we had the streamer mounted up a tree, using a 4m USB cable from the controller to the Pi, and a 1m USB from the Pi to the modem. The setup also included a USB hub (for a modem and AIMicro interface), and two Rode LavGo lavalier mics. It worked… for a while. But over time, we saw weird failures: the modem stopped being recognized, the hub was unreliable, etc.

Eventually, the culprit turned out to be the cables and the hub. I swapped in a sturdier USB hub and a thick 40cm USB cable between the RPi and the modem, and wrapped the connections where possible. I also replaced the power line with a new 4m USB cable. After that, everything started behaving again — even with the long 4m run, though with standard cables, that length is usually a weak point and might need replacement from time to time.

<br />

#### But then winter comes (and the Pi goes offline 😞)

<br />

Winter is a completely different story.

In summer, a 50W panel might be enough.
In winter? You might need four 120W panels — 480W total(!) — and a 120AH deep-cycle battery just to keep a device drawing 0.2A online.

**In the UK winter, the sun barely gets above the horizon. In early December it just peeks out, waves hello, and ducks back down.**

Here's a south-facing photo taken in late November, with the red dotted line roughly marking the sun's path.

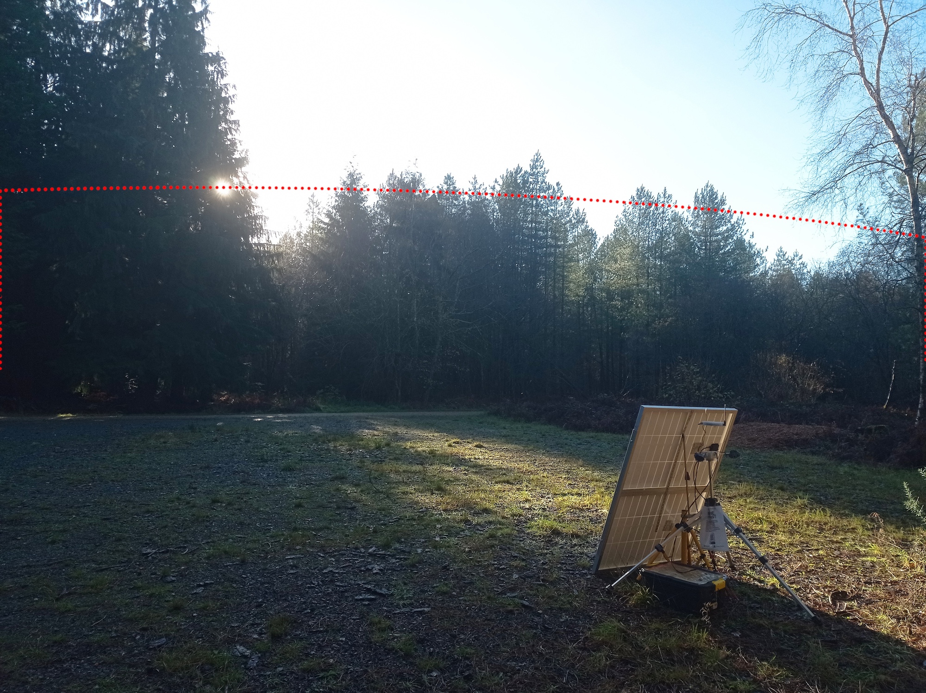
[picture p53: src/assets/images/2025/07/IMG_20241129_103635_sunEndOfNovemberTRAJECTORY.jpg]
Winter sun trajectory


As you can see from the sun’s path, even in a wide open space, the low sun angle means that distant trees can block direct sunlight for hours. That, plus the shorter days, changes everything.

And yes, direct sunlight makes a huge difference. Here’s a matrix of comparison shots to show what kind of light we’re talking about. Notice on the left how much sunlight is hitting the panel, and on the right, the measurements taken within seconds of the shot. All pictures taken on 29-Nov-2024 from 10.40AM to 11.30AM.

<br />

<table>
  <tr>
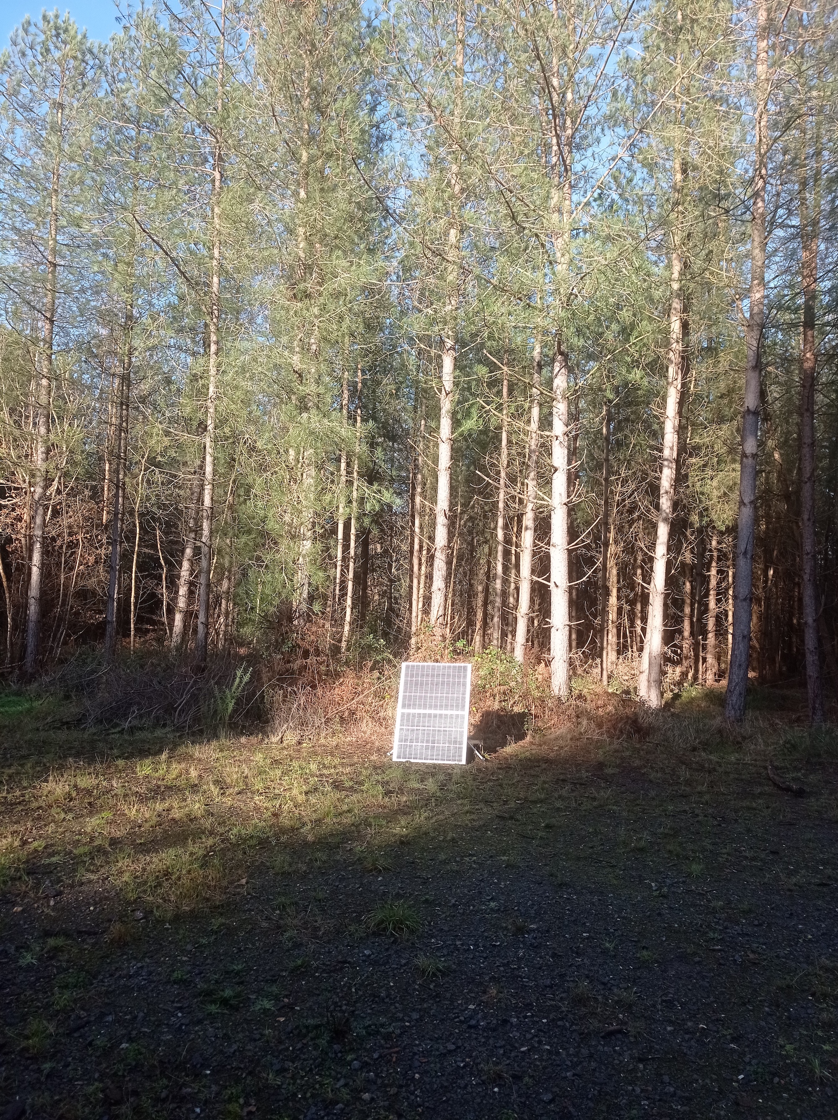
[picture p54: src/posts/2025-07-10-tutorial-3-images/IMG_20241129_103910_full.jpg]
    <td align="center">Direct sunlight - 2 x 120W panels<br /><br /></td>
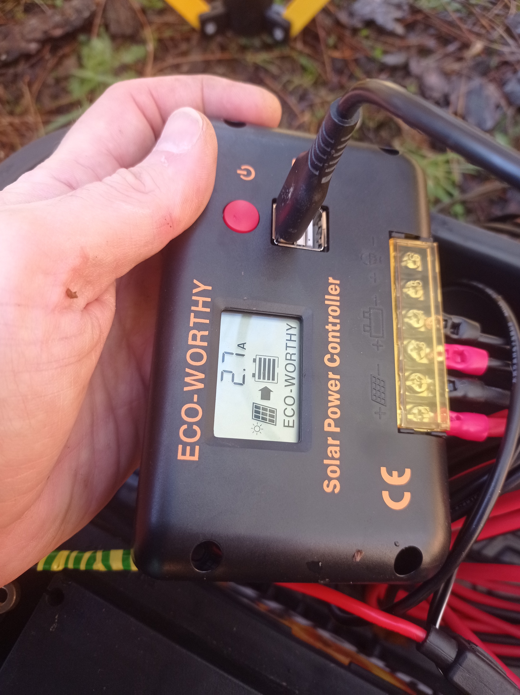
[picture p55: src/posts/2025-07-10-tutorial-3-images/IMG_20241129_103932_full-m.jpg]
    <td align="center">Direct sunlight - ampere reading<br /><br /></td>
  </tr>
  <tr>
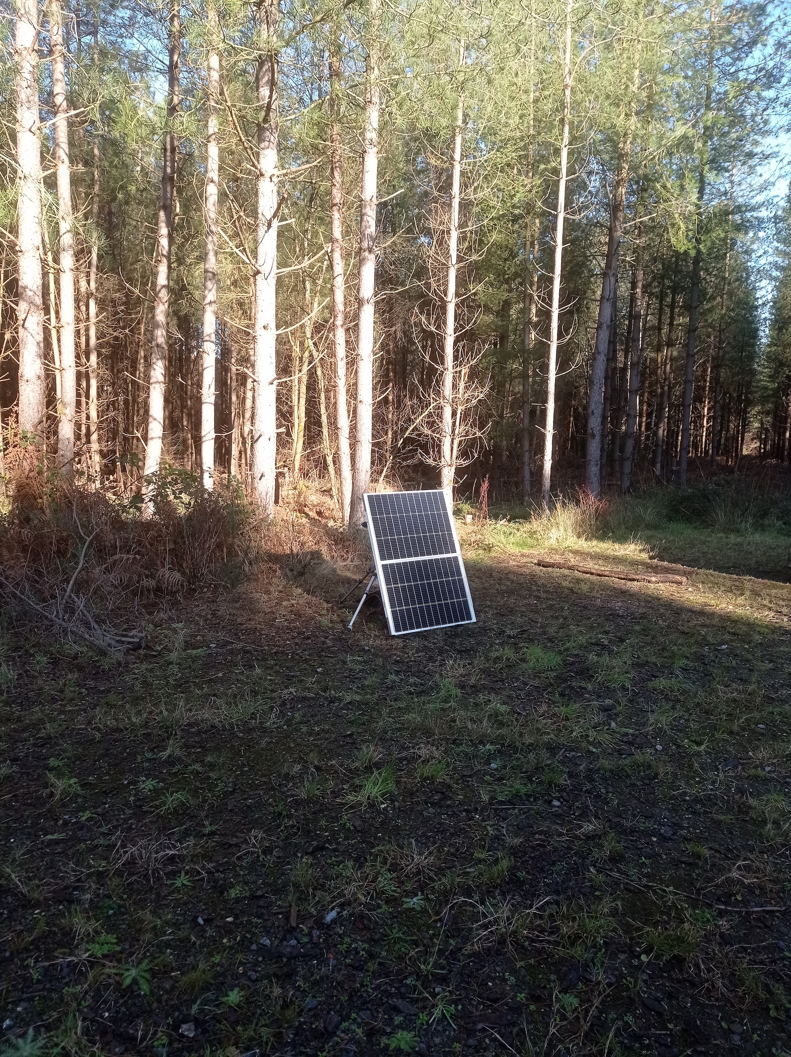
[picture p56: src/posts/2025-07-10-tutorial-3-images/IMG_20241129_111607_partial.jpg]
    <td align="center">Partial shade - 2 x 120W panels<br /><br /></td>
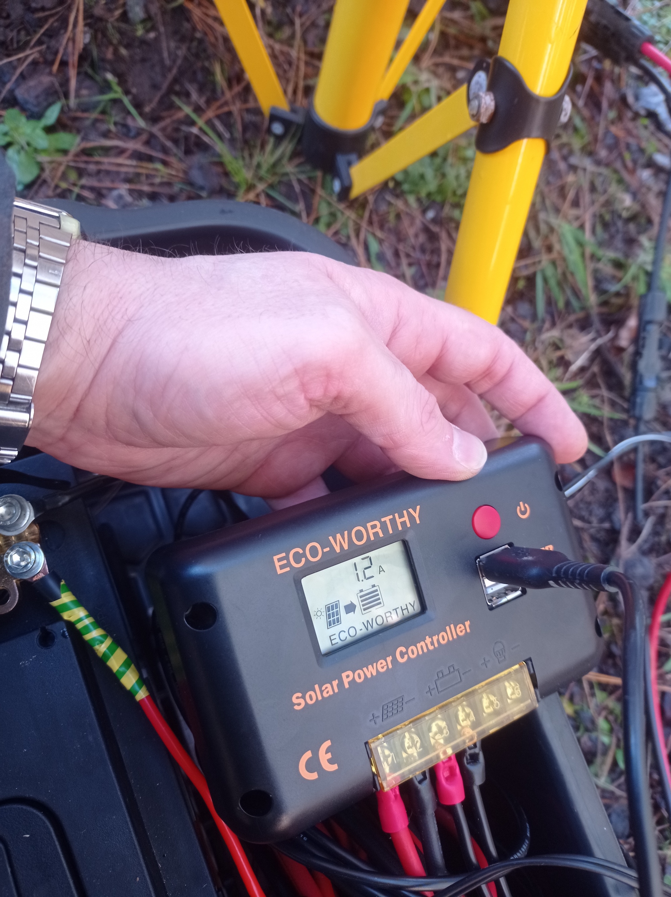
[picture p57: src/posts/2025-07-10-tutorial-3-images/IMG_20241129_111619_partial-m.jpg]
    <td align="center">Partial shade - ampere reading<br /><br /></td>
  </tr>
  <tr>
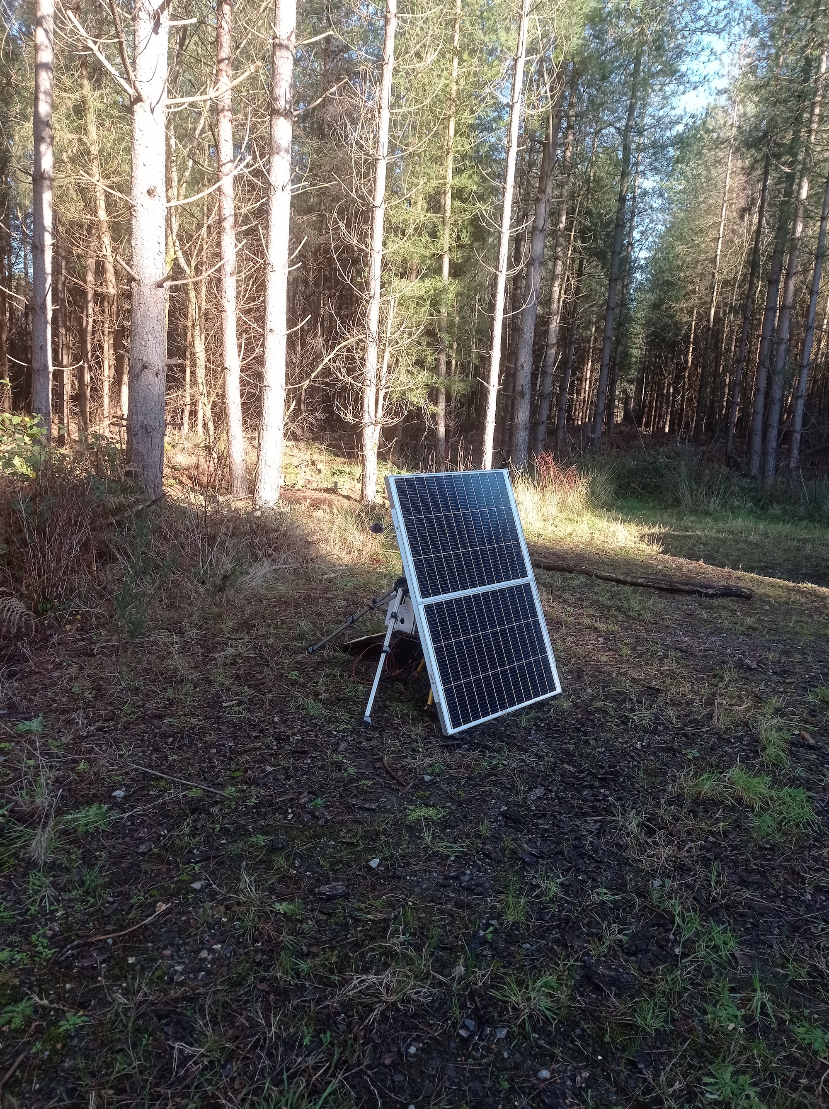
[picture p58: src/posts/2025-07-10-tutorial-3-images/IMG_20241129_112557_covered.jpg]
    <td align="center">Shade - 2 x 120W panels<br /><br /></td>
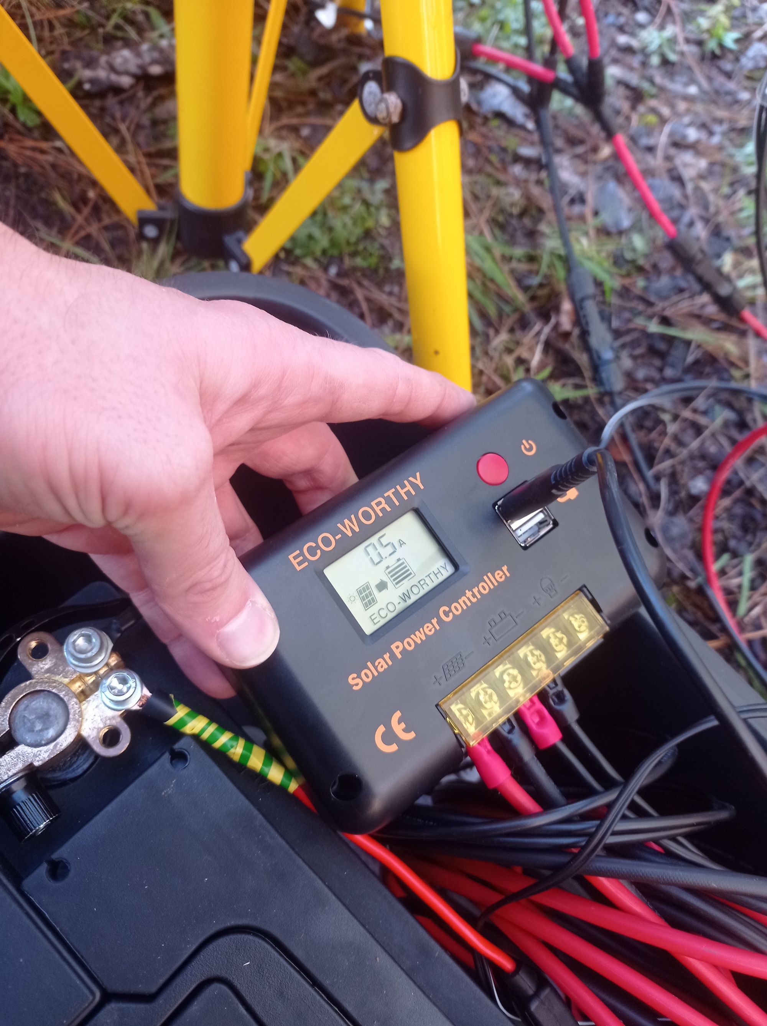
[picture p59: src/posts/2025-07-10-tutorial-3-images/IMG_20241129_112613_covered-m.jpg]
    <td align="center">Shade - ampere reading<br /><br /></td>
  </tr>
</table>

<br />

---

<br />

#### Adjust Your Panel Angle!

<br />

The angle of the solar panel matters a lot. You want the sunlight to hit it as close to perpendicular as possible. To get sunlight across all seasons, **it's essential that the panel faces south**. Even a little deviation can noticeably reduce power generation during winter months.

<br />

<table>
  <tr>
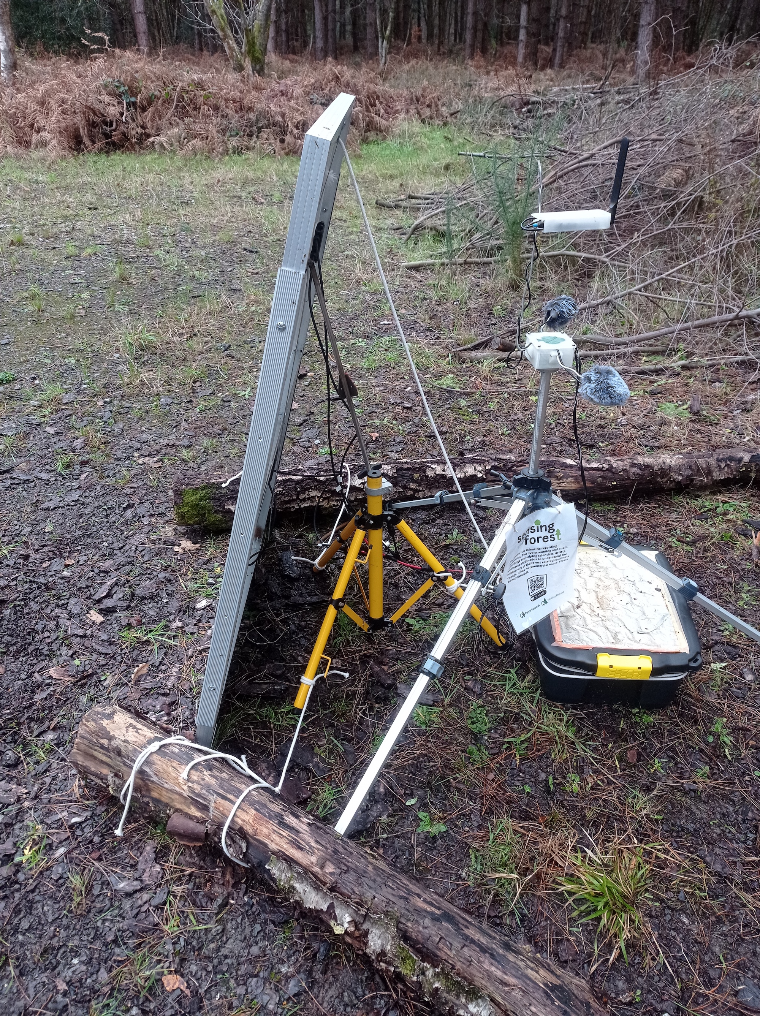
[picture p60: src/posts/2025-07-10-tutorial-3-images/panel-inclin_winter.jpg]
    <td align="center"><br/><strong>Winter</strong><br/>Nearly vertical</td>
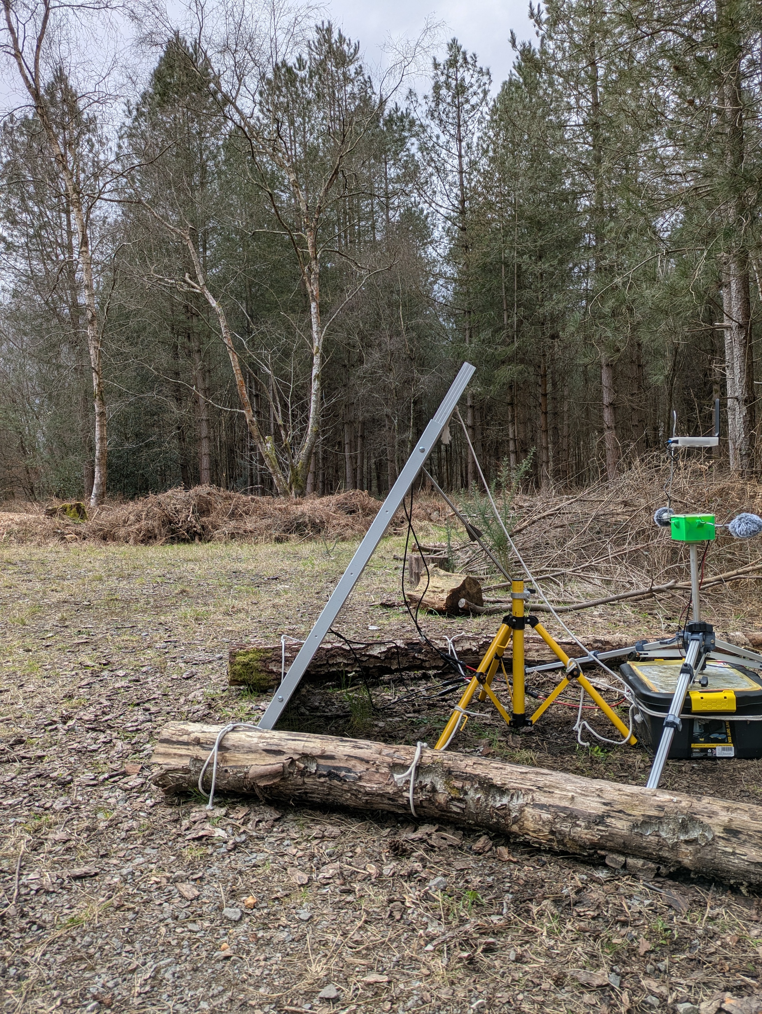
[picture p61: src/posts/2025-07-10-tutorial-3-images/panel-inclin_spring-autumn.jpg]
    <td align="center"><br/><strong>Autumn/Spring</strong><br/>Around 60°</td>
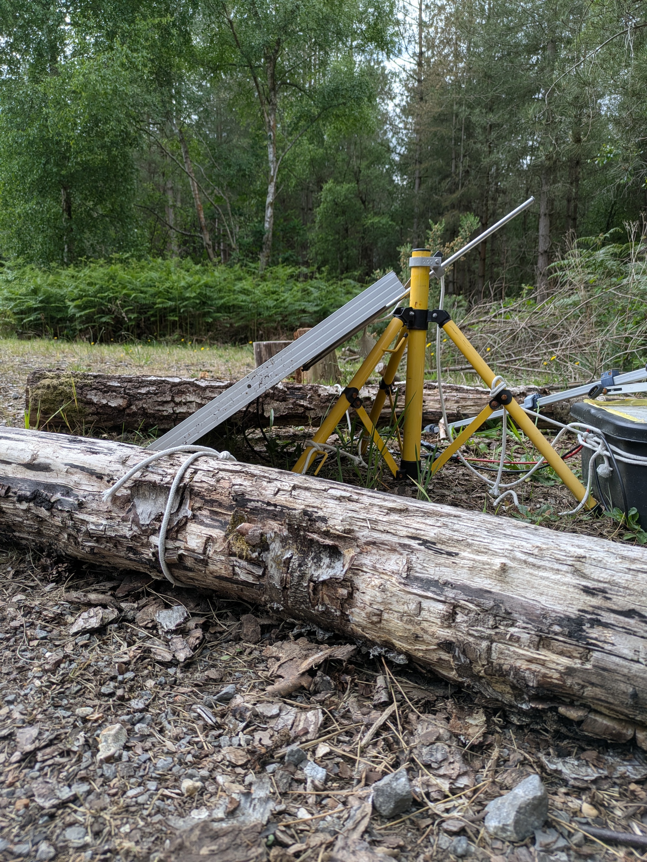
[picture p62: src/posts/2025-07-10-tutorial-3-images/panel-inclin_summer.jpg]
    <td align="center"><br/><strong>Summer</strong><br/>Around 45°</td>
  </tr>
</table>

<br />

---

<br />

#### And now some numbers - kindly brought to you by our battery sensor.

<br />

I set up voltage detection to run every 30 minutes. Below are graphs from two sunny days — 11 January and 11 May — showing the big difference in solar charging. Keep in mind that these graphs, especially the first one, also reflect the shading caused by surrounding trees, so they shouldn't be considered typical examples of full-sun conditions in an unobstructed field.

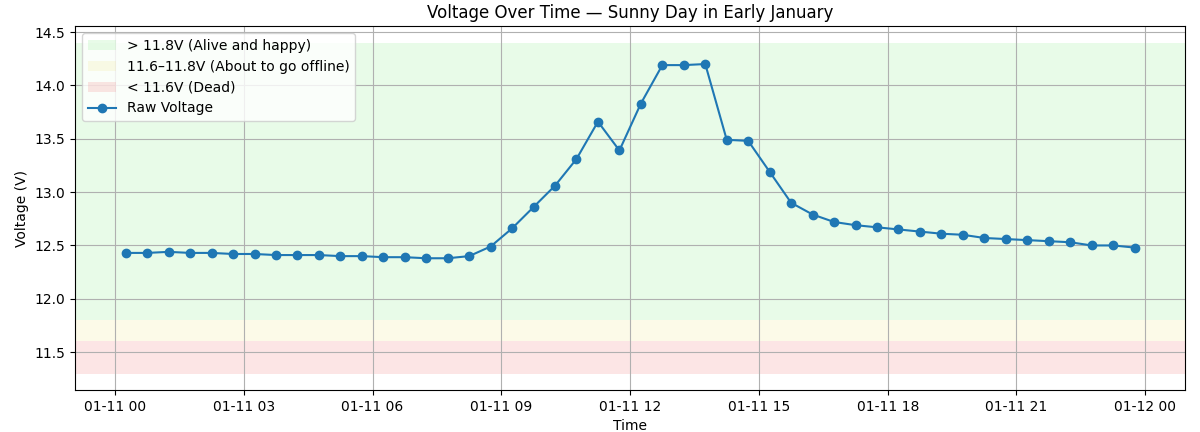
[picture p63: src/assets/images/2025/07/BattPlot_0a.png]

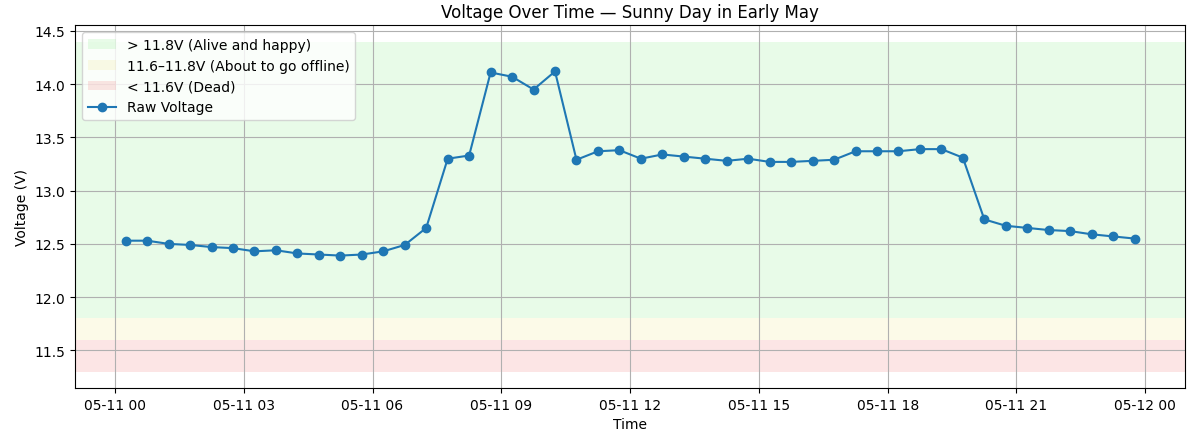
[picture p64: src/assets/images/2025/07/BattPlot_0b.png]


The background color shows the **battery status under load** — meaning with all the devices running. If you measure voltage when the battery is idle (nothing connected), the reading will be higher and not directly comparable. At 12.5V, the battery is fully charged, so fluctuations during solar charging don’t make much difference: as soon as the sun goes down, the voltage settles back around 12.5V and begins to discharge slowly.

You don’t want the battery sitting in the yellow or red zone for more than a week or two. If that happens, sulfation can occur — a process where lead sulfate crystals build up on the plates, permanently reducing the battery’s ability to hold charge.

And now a quick look at how I figured out the actual solar panel requirements. This is the battery log from the first 20 days of January:

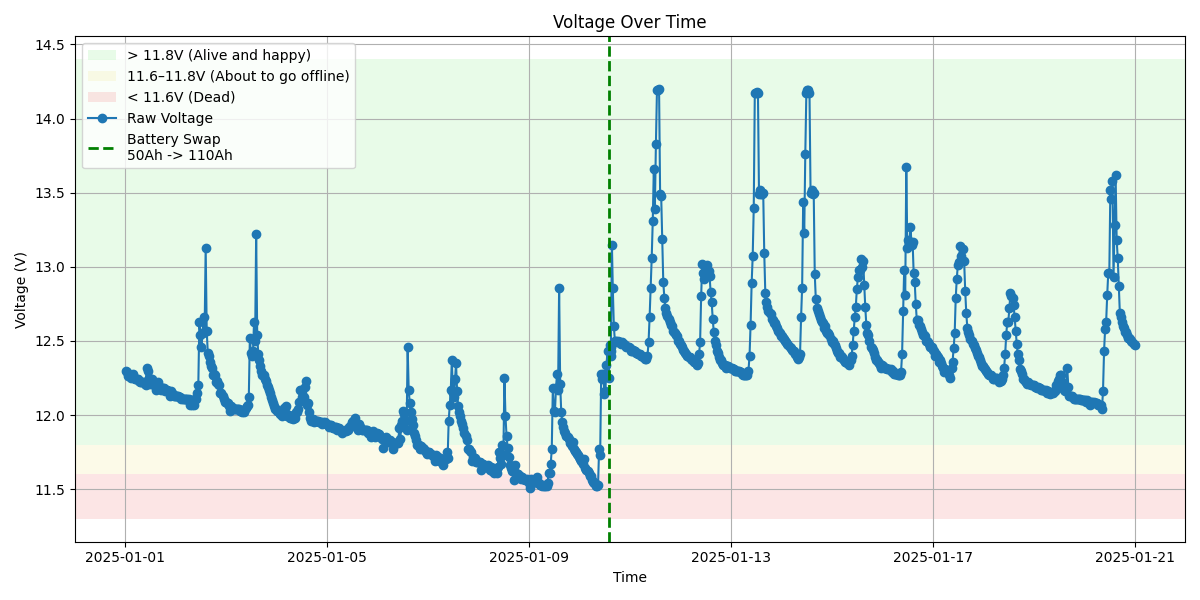
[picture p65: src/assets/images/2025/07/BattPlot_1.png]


The initial setup was based on a guess: 2 × 120W solar panels and a standard 50Ah flooded lead-acid car battery. It looked reasonable on paper — but as the graph shows, it wasn’t even close to enough for mid-winter conditions.

> **Note:** If you’re wondering why you still see data in the red / dead zone, it’s because the Pi will technically stay on down to around 11.5V, but below 11.6V, you should consider the system effectively dead. Why? Because things start to go offline — the modem is usually the first to fail, which means no stream, even if the Pi keeps logging battery status or recording audio for a little while longer.

The next attempt was to switch to an autocarvan battery 120Ah flooded lead-acid battery.

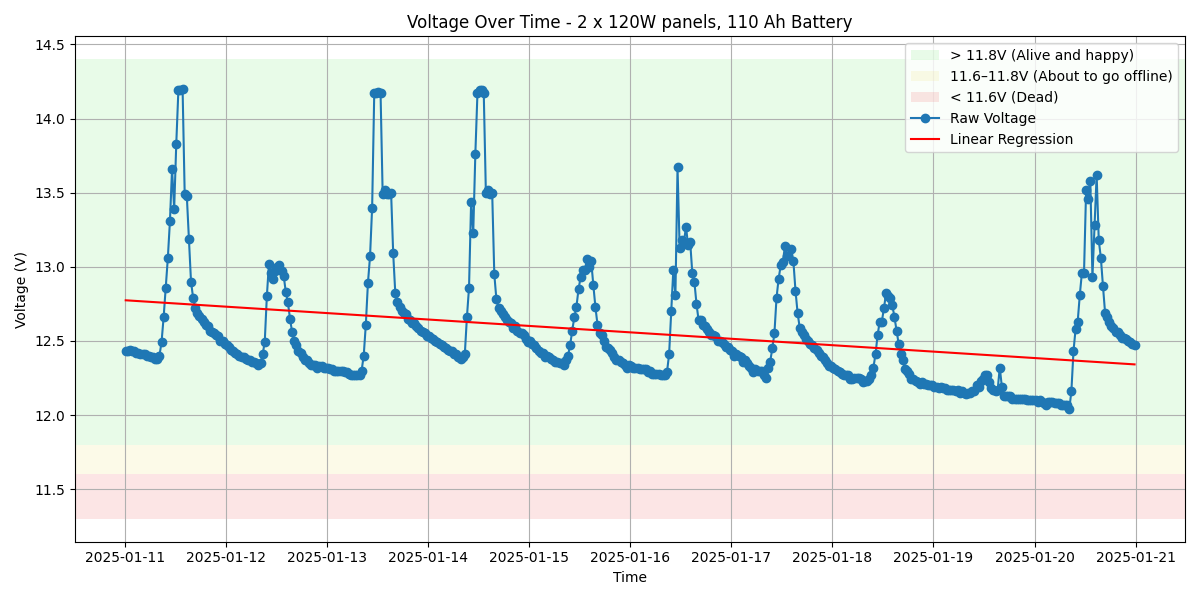
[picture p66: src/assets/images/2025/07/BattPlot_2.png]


This setup definitely improved the situation — and we were relatively lucky with the weather compared to the previous 10 days. Still, the linear regression was heading in the wrong direction. It might have just barely lasted until sunnier days, but I had already lost some recordings, so I decided to double the solar panel capacity: 

No more power issues from the solar system.

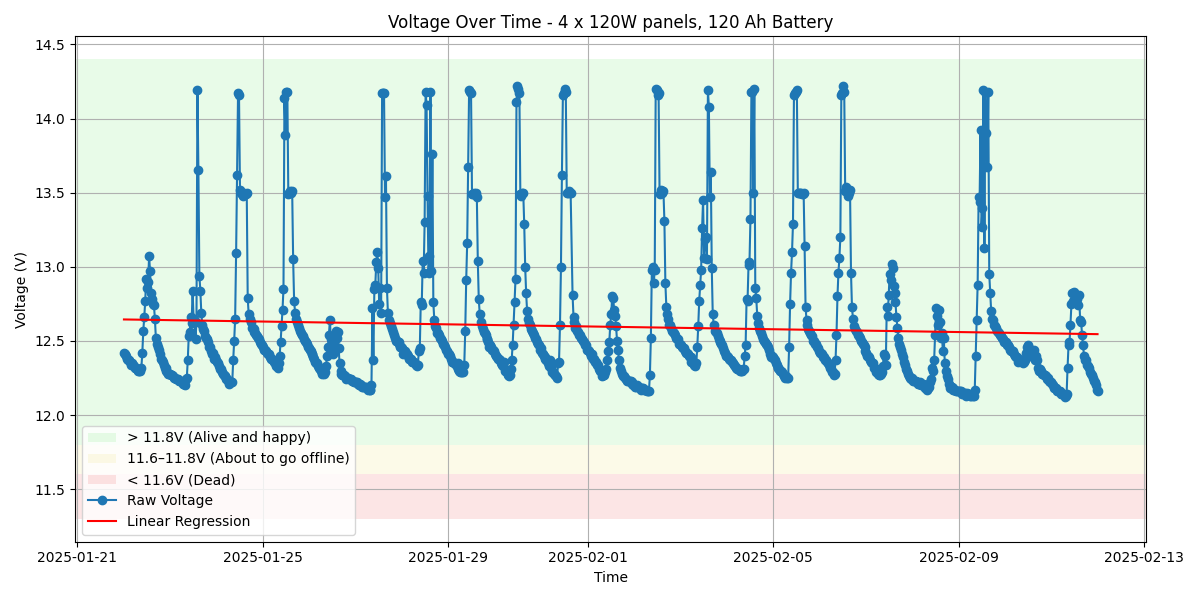
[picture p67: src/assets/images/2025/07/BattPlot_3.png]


It might seem like overkill to use 480W of solar panels and a 120Ah 12V battery to power a Raspberry Pi that draws just 0.2A — but UK winters offer very limited sunlight, and **unless you're in a perfectly open space, even trees or buildings 50 meters away can drastically reduce charging efficiency**. For non-critical setups in semi-open spaces, you could try 240W panels and a 120Ah battery and probably get away with it. But if **24/7 operation is critical in December and January**, this is the configuration I’d recommend: **4 × 120W solar panels + 120Ah lead-acid battery**.

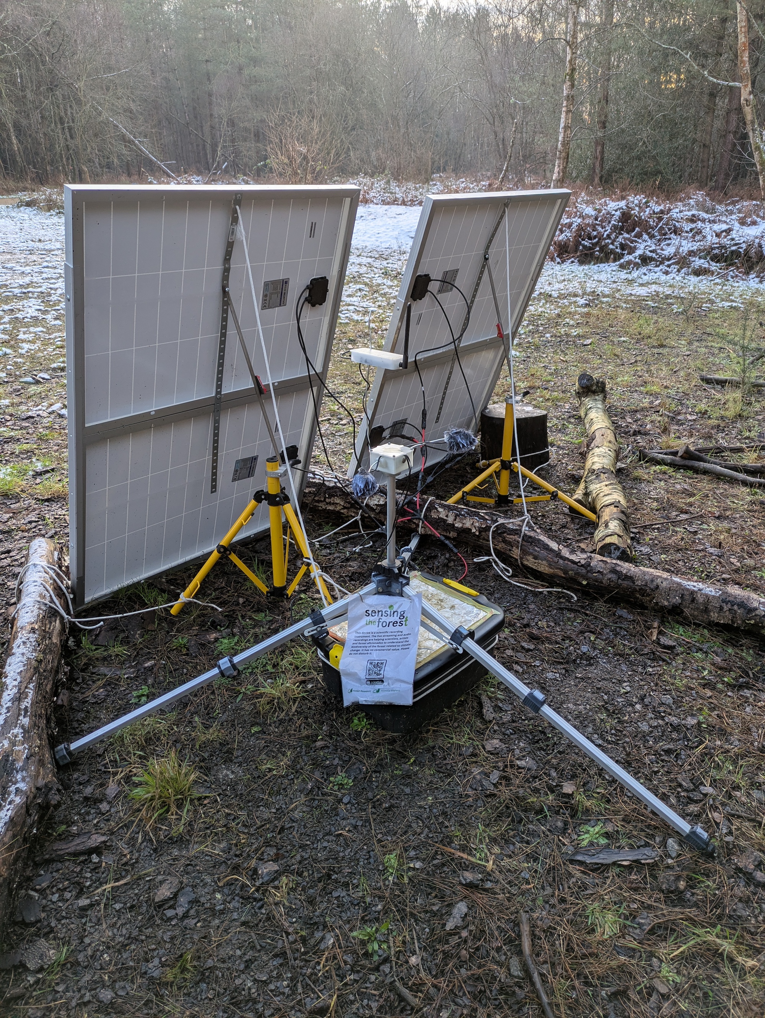
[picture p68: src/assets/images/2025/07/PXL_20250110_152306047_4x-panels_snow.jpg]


<br />

---

<br />

#### Summary of Lessons:

<br />

* In winter, you need **a really open space**, **facing south**, and ideally **no obstacles** around.
* In a partially open site (like in our photos) during the shortest days of the year, **480W worth of panels** was needed to stay online reliably.
* Adjusting the solar panels angle according to the season makes a big difference.
* **Under the canopy in winter? Forget it.**
  You’re better off running on a battery and replacing it every few weeks. We used a 120Ah caravan battery — it lasted about a month before needing a swap.
  You’ll need two batteries to rotate, a car battery charger at home, and a strong back — those things weigh 20kg each and are not much fun to drag through the woods. 

<br />

---
<br />
<br />
<br />

## Best of Nature-Induced Tech Failure  

The forest: beautiful, wild, and completely uninterested in helping your tech project succeed. Here's a curated selection of everything that went gloriously wrong — a blooper reel of our outdoor audio adventures.

**“No Bars in the Wild”**
Entire stretches of forest had absolutely no network coverage. Some spots *looked like* they had signal — just enough to give you false hope before dropping out mid-stream once we left the forest. The hunt went on…

**“From Hi-Fi to Harsh Noise”**
The -initially uncoated- MEMS microphone breakout corroded within weeks. What once captured birdsong now sounded like Merzbow doing a live set in a tin shed during a hailstorm.

**“Radio Interference Bonanza”**
Turns out, placing a modem too close to a Raspberry Pi creates enough RMI noise to disrupt everything. This problem was extreme with MEMS mics, definitely less with audio interfece and electrect mics (lavalier GO).

**“Gone with the Wind”**
Storms had a field day with our solar panels. Some were flipped, and a few spent quality time face-down in the mud. Our lesson? Tie everything to something heavier than air.

**“Modem Freeze: The Ancient Wisdom of Unplug and Replug”**
On rare occasions, the modem I used with the 4m power-cable streamer froze in a way that a simple Raspberry Pi reboot couldn’t fix, since rebooting keeps the modem powered. In those cases, the only cure was the classic, time-honored ritual: unplugging it and plugging it back in.

**“A Bug’s New Home”**
Large enough holes in a case often became a charming new apartment for insects. The 3D-printed microphone enclosures had an opening wide enough for the capsule to slide through — and before I thought about sealing it, a spider had already moved in! Actually the sounds were cool but the project had other requirements...

<br />

---

The contrast was stark. At home, everything worked perfectly on a cozy LAN. In the forest? It was survival of the fittest. Every single safety mechanism I coded felt like an overreaction... until it either solved a problem or wasn't enough.

Now, thanks to all that trial-by-error, the stream runs continuously with virtually zero intervention.

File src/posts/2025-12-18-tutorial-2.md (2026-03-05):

---
title: Phase 2 - A DIY Solar-Powered Home LAN Audio Streamer that Can Record Samples at Solar Times
date: 2025-12-18T10:00:00.000Z
excerpt: In this tutorial, I’ll walk you through the minimal steps to build a solar-powered home LAN streamer that can also automate recordings based on solar time.
permalink: /streamers/tutorial-2/
author: luigi-marino
draft: false
seo:
  title:
  description:
  image: 2025/12/birdfeeder.jpg
images: # relative to /src/assets/images/
  feature: 2025/12/birdfeeder.jpg
  thumb: 2025/12/birdfeeder.jpg
  align: # object-center (default) - other options at https://tailwindcss.com/docs/object-position
  height: h-auto # optional. Default = h-48 md:h-1/3
tags:
  - acoustic-ecology
  - development  
  - diy-streamer
  - do-it-yourself
  - locus-sonus
  - raspberry-pi
  - soundscapes
  - streamers
  - tutorials
---

## About this Tutorial

In this tutorial, I’ll walk you through the minimal steps to build a **solar-powered home LAN streamer** that can also **automate recordings based on solar time**. We’ll be using the code from [our repository](https://github.com/sensingtheforest/audio-streamer), but if you’d like to modify it for your own projects (and you’re absolutely encouraged to!), check out [this more advanced tutorial](https://sensingtheforest.github.io/streamers/tutorial-3/) for more details — including standalone solutions to some of the most annoying problems we ran into when deploying our streamers in the forest.

## Shopping List

* [ ] Raspberry Pi Zero 2W
* [ ] Micro SD card (any size, we used 256GB but calculate storage needs based on recording time)
* [ ] **Stereo Audio Input Options we tested**:

  * [ ] 2 × MEMS microphones with breakout (no audio interface needed, extremely cheap but low quality)
    **OR**
  * [ ] RØDE AI-Micro + 2 × Lavalier GO (most usb audio devices and lavalier mics will work)

<br />

### Solar Power Setup (optional)

* [ ] 1 × 120W solar panel
* [ ] Battery Charge Controller with 5V USB Output
* [ ] Any standard 12V car battery

## Hardware setup

This part is mostly up to you! If you’re feeling adventurous and want to 3d-print the movable mic cases shown in the pictures, the RPi case, understanting the solar power requirements, or add a battery sensor, check out the [more advanced tutorial](https://sensingtheforest.github.io/streamers/tutorial-3/). 

Here, I’ll skip the solar power wiring details. If you use a solar panel from brands like EcoWorthy or similar, it usually comes with a controller. All you need to do is connect the 12V battery and the solar panel to the controller, then use the stepped-down 5V USB output to power the Raspberry Pi. Just keep in mind that solar panels should face south, and if you don’t need perfect optimization according to the season, an incline of about 45° or a little more should do the job.

<br />

### Microphones

The USB audio devices are plug-and-play. Simply connect the micro-USB and run:

```bash
arecord -l
```

If you see something like USB Audio or the name of your device, you’re ready to move on to the software setup.

For the MEMS microphones, below a quick diagram illustrating the connections in a stereo configuration. (And yes... the wires aren't exactly drowing contest material...)

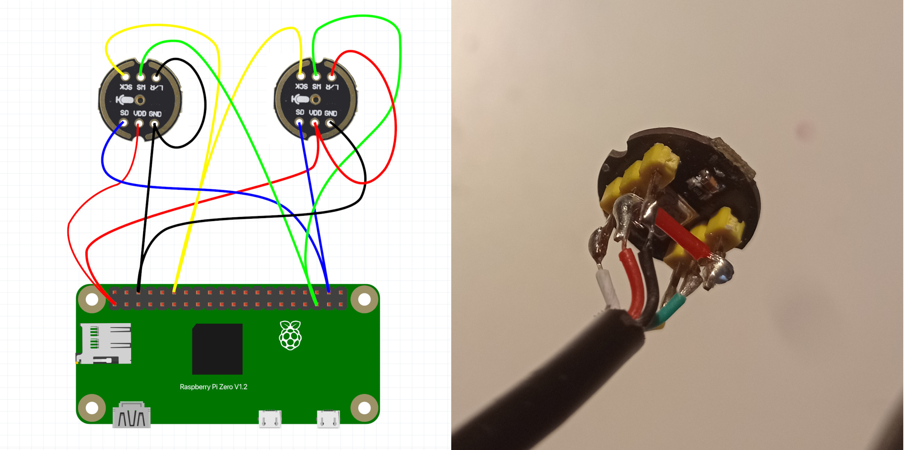
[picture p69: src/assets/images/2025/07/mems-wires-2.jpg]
mems-wires


Connect the MEMS microphones and proceed with the software setup — they aren’t plug-and-play, so we'll need the linux kernel headers and the drivers.

For a deeper explanation and tips on improving audio quality with the MEMS, or considerations about solar power requirements during winter refer again to the advanced tutorial. If your Raspberry Pi only powers itself and the two MEMS microphones, a single 120 W solar panel paired with a standard flooded lead-acid car battery should be sufficient even in winter. However, the seasonal difference is huge, and during months with limited sunlight (December and January), you may still experience periods offline.

## Case

Below are models for two case designs with suction cups (about 5 cm in diameter) for window mounting.

<br />

### Design Option 1

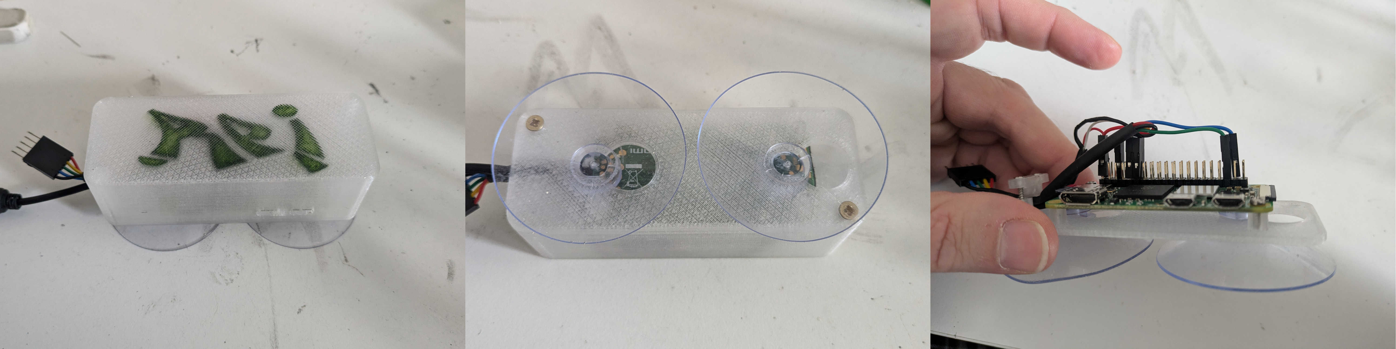
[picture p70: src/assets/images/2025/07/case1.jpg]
case1


The first is ultra-compact and fits only the RPi Zero, with just enough room for the header connections.
  
* [RPi0-Case1_FreeCAD-Project](/assets/3d-print/rpi-zero_suction-cup-1.FCStd)

<br />

#### Meshes

* [Case1-Top](/assets/3d-print/rpi0-case_suctioncap-1_TOP.stl)
* [Case1-Bottom](/assets/3d-print/rpi0-case_suctioncap-1_BOTTOM.stl)

<br />

### Design Option 2

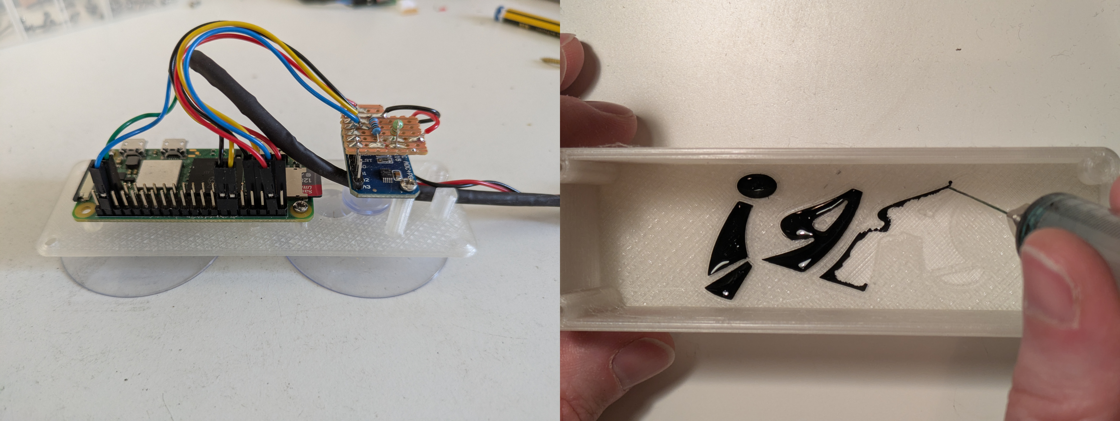
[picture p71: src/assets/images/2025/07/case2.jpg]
case2


The second also includes space for an ADS1115 battery sensor — very handy when running on solar power!

And should you ask the following research question: “Why does it look like a throwback to 90s hip-hop???”

We can only hope that future research and the advancement of cutting-edge technologies, will one day shed light on this most essential inquiry.

* [RPi0-Case2_FreeCAD-Project](/assets/3d-print/rpi0-case_ads1115_suction-cup.FCStd)

<br />

#### Meshes

* [Case2-Top](/assets/3d-print/rpi0-case_ads1115_suction-cup_TOP.stl)
* [Case2-Bottom](/assets/3d-print/rpi0-case_ads1115_suction-cup_BOTTOM.stl)

## Software setup

Just a slightly more commented version of the steps described in our [README.md](https://github.com/sensingtheforest/audio-streamer/blob/main/README.md) file in the repo.

<br />

### Prerequisites

If using MEMS microphones, enable I2S by editing the config file:

   ```bash
   sudo nano /boot/firmware/config.txt
   ```
   Add the following line at the end:
   ```bash
   dtparam=i2s=on
   ```

<br />

### Setup

1. Download the project folder to your Raspberry Pi's home directory. From the home folder:
   ```bash
   sudo apt update
   sudo apt install git
   git clone https://github.com/sensingtheforest/audio-streamer.git
   ```
2. Install all the necessary libraries.
   * Grant execute permission to the scripts in the project folder:
   ```bash
   cd audio-streamer
   find . -type f \( -name "*.sh" -o -name "*.py" \) -exec chmod +x {} \;
   ```
   * Now run the install script:
   ```bash
   ./install.sh
   ```
   * When prompted, say yes to configure Icecast2. After that, you can just use the default settings. If you change the default passwords, make sure to remember them — you’ll need them later for the Icecast2 config file. When prompted to configure msmtp (email app), and asked that confusing question, just go with the default no.
   * Say yes to reboot — this is the final step of the installer. If you changed the kernel headers setting in installer.sh, the installer will finish without rebooting.
   * **Note**: The script should install all required packages from the repositories. All the packages are listed in the script. There are some parameters at the beginning of install.sh   you can set to spare some time, otherwise it will do a full OS upgrade and compile the latest darkice version. This may take a while - get a cup of tea... or two... 
3. For MEMS microphones, install drivers:
   ```bash
   ./mems-drivers.sh
   ```
   * Reboot when prompted (type `y`).
   * **Note**: If not using MEMS microphones, skip to step 4. 
4. Set up the microphone:
   * Open the setup script:
   ```bash
   sudo nano mic-setup___o.sh
   ```
   * Set DEVICE and FORMAT to match your microphone. You can find your device name running:
   ```bash
   arecord -l
   ```
   * Save the file as mic-setup.sh (remove "___o") and run it:
   ```bash
   sudo mv mic-setup___o.sh mic-setup.sh 
   ./mic-setup.sh
   ```
   * A 10-second recording test should start. You should see volume meters (or a vague memory of them) moving. Check for `mic-test.wav` in the project folder.
   * You can adjust the microphone capture volume in alsamixer. Run:
   ```bash
   alsamixer
   ```
   To see the fader, click on `F6: Select your soundcard`, and then show all volume controls with `F5: All`.

   If you want to repeat the test and observe the signal levels, run:
   ```bash
   arecord -d 10 -D mic_out_shared -c 2 -r 44100 -f S16_LE -t wav -V stereo -v mic-test.wav
   ```
5. Configure settings:
   * Edit all remaining files ending in `"___o"` with your settings. Settings are commented inside each file (`msmtprc___o.txt` is optional, see step 7).
   * Save them without `"___o"` (e.g., edit `common___o.sh` and save as `common.sh`).
   * **Note**: You can keep the originals using `cp` instead of renaming them with `mv`, only those without `"___o"` will be used. I use mv to see right away which ones I've already edited.
6. Test the stream:
   ```bash
   ./stream.sh
   ```
   * If everything is set up correctly, you should be able to access the stream through your Icecast2 server address, which typically looks something like `192.168.0.172:8000`.
If you’re unsure about the address, check which IP has been assigned to your Raspberry Pi from your home modem’s admin page.
   * **Note**: This assumes that `darkice.cfg` has been set up correctly, there are no errors in the terminal, and the last line ends with `SCHED_FIFO`.
7. (optional) Enable email operations:
   * Obtain an App Password from your email account (we used Gmail). **Don’t use your Google account password!** The app password is a special password created just for this purpose.
   * Update the *'from'*, *'user'*, and *'password'* fields with your own credentials.
   * Save this file as a hidden configuration in your home folder and set the appropriate permissions.
   ```bash
   sudo mv msmtprc___o.txt ~/.msmtprc
   chmod 600 ~/.msmtprc
   ```
   * Enable IMAP on your email account to allow the Raspberry Pi to download attachments from your emails and receive remote updates.
8. (optional) Set up cronjobs for automatic problem solving and sending the logs:
   * Open the crontab editor 
   ```bash
   crontab -e
   ```
   * Copy and paste this content in the crontab and save.
   ```bash 
   # The environment for cron jobs is more limited than your normal shell environment.
   # Setting the PATH variable here ensures proper path resolution for all cron-executed commands and scripts.
   export PATH=$PATH:/usr/local/sbin:/usr/local/bin:/usr/sbin:/usr/bin:/sbin:/bin

   # By default, if a cron job generates output (stdout or stderr), 
   # it's emailed to the user who owns the crontab.
   # Setting MAILTO to an empty string suppresses these emails.
   MAILTO=""

   # Health check every hour. Append states on uptime.log
   30 * * * * $HOME/audio-streamer/monitor.sh

   # At 3AM: check if darkice is streaming, if not reboot. 
   # Rebooting sends the log email so too often can be annoying... 
   0 3 * * * $HOME/audio-streamer/nuclear-option.sh

   ### (optional email operations, for this you need step 7)
   # At 9PM: send the log file and limit the lines to the last 50000.
   0 9 * * * $HOME/audio-streamer/rotate-log.sh; sleep 5; $HOME/audio-streamer/send-email.sh
   # Every 4 hours: look for an email with a specific subject, copy its attachments to the main folder, then run blank.sh.
   0 */4 * * * $HOME/audio-streamer/venv/bin/python $HOME/audio-streamer/update-code.py; sleep 10; $HOME/audio-streamer/blank.sh
   ```
     
9. (optional) Create boot service to start the streamer when you turn it on. **Don't use the @reboot line in crontab!** That is going to be trouble...
   * Open `boot.service.txt`
   ```bash
   sudo nano boot.service.txt
   ```
   * Replace the placeholder values in the *'ExecStart'*, *'User'*, and *'WorkingDirectory'* fields with your actual username. Save and exit the editor.
   * Remove the extension and move the file to the correct systemd directory:
   ```bash
   sudo mv boot.service.txt /etc/systemd/system/boot.service
   ```
   * Reload systemd, enable the service to run at boot, and reboot the system:
   ```bash
   sudo systemctl daemon-reload
   sudo systemctl enable boot.service
   sudo reboot
   ```
   * After rebooting, you can check if the service is running properly with:
   ```bash
   sudo systemctl status boot.service
   ```
10. ENJOY!

<br />

---

Our code automatically records 5-minute samples at sunrise, solar noon, sunset, and once during the night (between sunset and sunrise). You'll find the wav files inside `audio-streamer/audio`.

You can adjust the solar times in `solar-crontab.py`, and change the recording duration in `common.sh`, where you’ll also find several other system parameters. Using these parameters, you can deactivate the recording feature by changing `RECORD=1` to `RECORD=0` (you'll need to reboot, or manually kill the active record screen session). For more details, refer again to the [advanced tutorial](https://sensingtheforest.github.io/streamers/tutorial-3/).

And yes, after more than 800 hours of uninterrupted, solar-powered streaming and recording, I’d say it’s safe to call it reliable 🎉

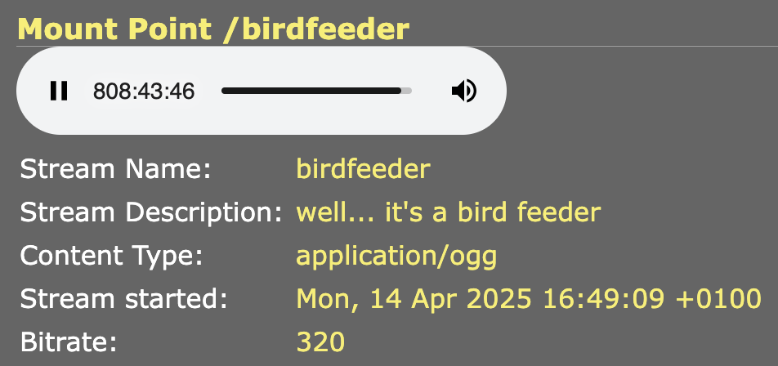
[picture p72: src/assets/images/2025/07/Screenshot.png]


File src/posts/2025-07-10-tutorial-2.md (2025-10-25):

---
title: Phase 2
date: 2025-07-10T10:00:00.000Z
excerpt: In this tutorial, I will ...
permalink: /2025/07/10/phase-2/
author: luigi-marino
draft: true
seo:
  title:
  description:
  image: 2025/07/placeholder.jpg
images: # relative to /src/assets/images/
  feature: 2025/07/placeholder.jpg
  thumb: 2025/07/placeholder.jpg
  align: # object-center (default) - other options at https://tailwindcss.com/docs/object-position
  height: h-auto # optional. Default = h-48 md:h-1/3
tags:
  - acoustic-ecology
  - development  
  - locus-sonus
  - raspberry-pi
  - soundscapes
  - streamers
  - tutorials
---

## About this Tutorial

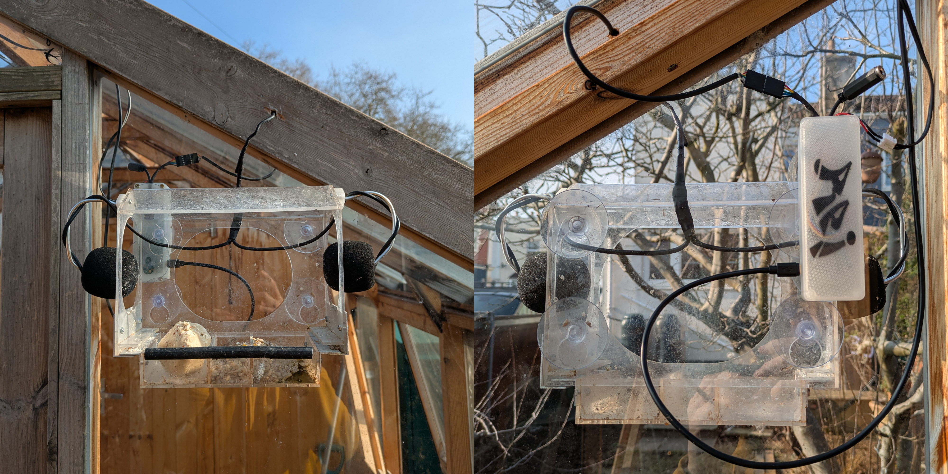
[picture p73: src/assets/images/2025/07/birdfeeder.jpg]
birdfeeder


In this tutorial, I’ll walk you through the minimal steps to build a **solar-powered home LAN streamer** that can also **automate recordings based on solar time**. We’ll be using the code from [our repository](https://github.com/sensingtheforest/audio-streamer), but if you’d like to modify it for your own projects (and you’re absolutely encouraged to!), check out [this more advanced tutorial](https://sensingtheforest.github.io/streamers/tutorial-3/) for more details — including standalone solutions to some of the most annoying problems we ran into when deploying our streamers in the forest.

## Shopping List

* [ ] Raspberry Pi Zero 2W
* [ ] Micro SD card (any size, we used 256GB but calculate storage needs based on recording time)
* [ ] **Stereo Audio Input Options we tested**:

  * [ ] 2 × MEMS microphones with breakout (no audio interface needed, extremely cheap but low quality)
    **OR**
  * [ ] RØDE AI-Micro + 2 × Lavalier GO (most usb audio devices and lavalier mics will work)

#### Solar Power Setup (optional)
* [ ] 1 × 120W solar panel
* [ ] Battery Charge Controller with 5V USB Output
* [ ] Any standard 12V car battery

## Hardwere setup

This part is mostly up to you! If you’re feeling adventurous and want to 3d-print the movable mic cases shown in the pictures, the RPi case, understanting the solar power requirements, or add a battery sensor, check out the [more advanced tutorial](https://sensingtheforest.github.io/streamers/tutorial-3/). 

Here, I’ll skip the solar power wiring details. If you use a solar panel from brands like EcoWorthy or similar, it usually comes with a controller. All you need to do is connect the 12V battery and the solar panel to the controller, then use the stepped-down 5V USB output to power the Raspberry Pi. Just keep in mind that solar panels should face south, and if you don’t need perfect optimization according to the season, an incline of about 45° or a little more should do the job.

#### Microphones

The USB audio devices are plug-and-play. Simply connect the micro-USB and run:

```bash
arecord -l
```

If you see something like USB Audio or the name of your device, you’re ready to move on to the software setup.

For the MEMS microphones, below a quick diagram illustrating the connections in a stereo configuration. (And yes... the wires aren't exactly drowing contest material...)

mems-wires

Connect the MEMS microphones and proceed with the software setup — they aren’t plug-and-play, so we'll need the linux kernel headers and the drivers.

For a deeper explanation and tips on improving audio quality with the MEMS, or considerations about solar power requirements during winter refer again to the advanced tutorial. If your Raspberry Pi only powers itself and the two MEMS microphones, a single 120 W solar panel paired with a standard flooded lead-acid car battery should be sufficient even in winter. However, the seasonal difference is huge, and during months with limited sunlight (December and January), you may still experience periods offline.

#### Case

Below are models for two case designs with suction cups (about 5 cm in diameter) for window mounting.

* The first is ultra-compact and fits only the RPi Zero, with just enough room for the header connections.
  
[RPi0-Case1_FreeCAD-Project](../../src/assets/3d-print/rpi-zero_suction-cup-1.FCStd)<br />

Meshes:<br />
[Case-Top](../../src/assets/3d-print/rpi0-case_suctioncap-1_TOP.stl)<br />
[Case-Bottom](../../src/assets/3d-print/rpi0-case_suctioncap-1_BOTTOM.stl)<br />

case1
  
* The second also includes space for an ADS1115 battery sensor — very handy when running on solar power!

case2

And should you ask the following research question: “Why does it look like a throwback to 90s hip-hop???”

We can only hope that future research and the advancement of cutting-edge technologies, will one day shed light on this most essential inquiry.

## Software setup

Just a slightly more commented version of the steps described in our README.md file in the repo.

#### Prerequisites

If using MEMS microphones, enable I2S by editing the config file:
   ```
   sudo nano /boot/firmware/config.txt
   ```
   Add the following line at the end:
   ```
   dtparam=i2s=on
   ```
#### Setup

1. Download the project folder to your Raspberry Pi's home directory. From the home folder:
   ```
   sudo apt update
   sudo apt install git
   git clone https://github.com/sensingtheforest/audio-streamer.git
   ```
2. Install all the necessary libraries.
   * Grant execute permission to the scripts in the project folder:
   ```
   cd audio-streamer
   find . -type f \( -name "*.sh" -o -name "*.py" \) -exec chmod +x {} \;
   ```
   * Now run the install script:
   ```
   ./install.sh
   ```
   * When prompted, say yes to configure Icecast2. After that, you can just use the default settings. If you change the default passwords, make sure to remember them — you’ll need them later for the Icecast2 config file. When prompted to configure msmtp (email app), and asked that confusing question, just go with the default no.
   * Say yes to reboot — this is the final step of the installer. If you changed the kernel headers setting in installer.sh, the installer will finish without rebooting.
   * **Note**: The script should install all required packages from the repositories. All the packages are listed in the script. There are some parameters at the beginning of install.sh   you can set to spare some time, otherwise it will do a full OS upgrade and compile the latest darkice version. This may take a while - get a cup of tea... or two... 
3. For MEMS microphones, install drivers:
   ```
   ./mems-drivers.sh
   ```
   * Reboot when prompted (type `y`).
   * **Note**: If not using MEMS microphones, skip to step 4. 
4. Set up the microphone:
   * Open the setup script:
   ```
   sudo nano mic-setup___o.sh
   ```
   * Set DEVICE and FORMAT to match your microphone. You can find your device name running:
   ```
   arecord -l
   ```
   * Save the file as mic-setup.sh (remove "___o") and run it:
   ```
   sudo mv mic-setup___o.sh mic-setup.sh 
   ./mic-setup.sh
   ```
   * A 10-second recording test should start. You should see volume meters (or a vague memory of them) moving. Check for `mic-test.wav` in the project folder.
   * You can adjust the microphone capture volume in alsamixer. Run:
   ```
   alsamixer
   ```
   To see the fader, click on "F6: Select your soundcard", and then show all volume controls with "F5: All". <br>
   If you want to repeat the test and observe the signal levels, run:
   ```
   arecord -d 10 -D mic_out_shared -c 2 -r 44100 -f S16_LE -t wav -V stereo -v mic-test.wav
   ```
5. Configure settings:
   * Edit all remaining files ending in "___o" with your settings. Settings are commented inside each file (msmtprc___o.txt is optional, see step 7).
   * Save them without "___o" (e.g., edit `common___o.sh` and save as `common.sh`).
   * **Note**: You can keep the originals using `cp` instead of renaming them with `mv`, only those without `"___o"` will be used. I use mv to see right away which ones I've already edited.
6. Test the stream:
   ```
   ./stream.sh
   ```
   * If everything is set up correctly, you should be able to access the stream through your Icecast2 server address, which typically looks something like 192.168.0.172:8000.
If you’re unsure about the address, check which IP has been assigned to your Raspberry Pi from your home modem’s admin page.
   * **Note**: This assumes that `darkice.cfg` has been set up correctly, there are no errors in the terminal, and the last line ends with `SCHED_FIFO`.
7. (optional) Enable email operations:
   * Obtain an App Password from your email account (we used Gmail). **Don’t use your Google account password!** The app password is a special password created just for this purpose.
   * Update the 'from', 'user', and 'password' fields with your own credentials.
   * Save this file as a hidden configuration in your home folder and set the appropriate permissions.
   ```
   sudo mv msmtprc___o.txt ~/.msmtprc
   chmod 600 ~/.msmtprc
   ```
   * Enable IMAP on your email account to allow the Raspberry Pi to download attachments from your emails and receive remote updates.
8. (optional) Set up cronjobs for automatic problem solving and sending the logs:
   * Open the crontab editor 
   ```
   crontab -e
   ```
   * Copy and paste this content in the crontab and save.
   ``` 
   # The environment for cron jobs is more limited than your normal shell environment.
   # Setting the PATH variable here ensures proper path resolution for all cron-executed commands and scripts.
   export PATH=$PATH:/usr/local/sbin:/usr/local/bin:/usr/sbin:/usr/bin:/sbin:/bin

   # By default, if a cron job generates output (stdout or stderr), 
   # it's emailed to the user who owns the crontab.
   # Setting MAILTO to an empty string suppresses these emails.
   MAILTO=""

   # Health check every hour. Append states on uptime.log
   30 * * * * $HOME/audio-streamer/monitor.sh

   # At 3AM: check if darkice is streaming, if not reboot. 
   # Rebooting sends the log email so too often can be annoying... 
   0 3 * * * $HOME/audio-streamer/nuclear-option.sh

   ### (optional email operations, for this you need step 7)
   # At 9PM: send the log file and limit the lines to the last 50000.
   0 9 * * * $HOME/audio-streamer/rotate-log.sh; sleep 5; $HOME/audio-streamer/send-email.sh
   # Every 4 hours: look for an email with a specific subject, copy its attachments to the main folder, then run blank.sh.
   0 */4 * * * $HOME/audio-streamer/venv/bin/python $HOME/audio-streamer/update-code.py; sleep 10; $HOME/audio-streamer/blank.sh
   ```
     
9. (optional) Create boot service to start the streamer when you turn it on. **Don't use the @reboot line in crontab!** That is going to be trouble...
   * Open boot.service.txt
   ```
   sudo nano boot.service.txt
   ```
   * Replace the placeholder values in the 'ExecStart', 'User', and 'WorkingDirectory' fields with your actual username. Save and exit the editor.
   * Remove the extension and move the file to the correct systemd directory:
   ```
   sudo mv boot.service.txt /etc/systemd/system/boot.service
   ```
   * Reload systemd, enable the service to run at boot, and reboot the system:
   ```
   sudo systemctl daemon-reload
   sudo systemctl enable boot.service
   sudo reboot
   ```
   * After rebooting, you can check if the service is running properly with:
   ```
   sudo systemctl status boot.service
   ```
10. ENJOY!

---

Our code automatically records 5-minute samples at sunrise, solar noon, sunset, and once during the night (between sunset and sunrise). You'll find the wav files inside `audio-streamer/audio`.
You can adjust the solar times in `solar-crontab.py`, and change the recording duration in `common.sh`, where you’ll also find several other system parameters. Using these parameters, you can deactivate the recording feature by changing `RECORD=1` to `RECORD=0` (you'll need to reboot, or manually kill the active record screen session). For more details, refer again to the [advanced tutorial](https://sensingtheforest.github.io/streamers/tutorial-3/).

And yes, after more than 800 hours of uninterrupted, solar-powered streaming and recording, I’d say it’s safe to call it reliable 🎉

case2

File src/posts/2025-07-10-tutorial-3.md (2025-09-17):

---
title: A DIY Solar-Powered Audio Streamer that Can Record Samples at Solar Times
date: 2025-07-10T10:00:00.000Z
excerpt: In this tutorial, I explain how to build the exact same solar-powered audio streamers we use in the forest.
permalink: /2025/07/10/phase-3/
author: luigi-marino
draft: true
seo:
  title:
  description:
  image: 2025/07/placeholder.jpg
images: # relative to /src/assets/images/
  feature: 2025/07/placeholder.jpg
  thumb: 2025/07/placeholder.jpg
  align: # object-center (default) - other options at https://tailwindcss.com/docs/object-position
  height: h-auto # optional. Default = h-48 md:h-1/3
tags:
  - acoustic-ecology
  - development  
  - locus-sonus
  - raspberry-pi
  - soundscapes
  - streamers
  - tutorials
---

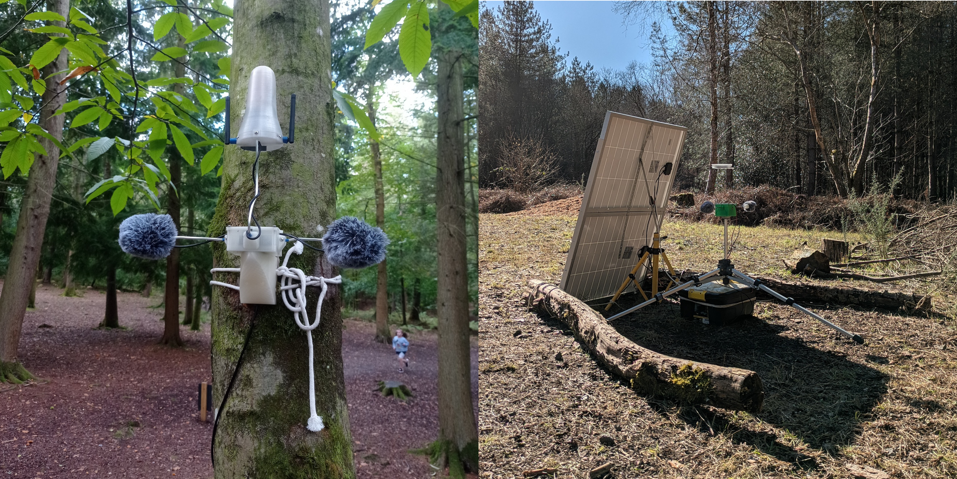
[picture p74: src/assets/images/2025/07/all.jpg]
cover


## About this Tutorial

In this tutorial, I explain how to build the exact same solar-powered audio streamers we use in the forest.

Getting to the final version was a bumpy ride, so this guide offers more of a behind-the-scenes look at the challenges I faced, how I solved them, technical insights into the code, and real-world solar power data to ensure continuous operation.

But don’t worry! If you just want to get started quickly, there’s a more direct how-to guide: first, check the **shopping list**, then follow the instructions in the **README file in our repository**. If something doesn’t work or you’re not sure what’s going on, come back here for detailed explanations and tips.  

As everyone seems to focus on large AI models that require supercomputers accessible only to a few, this project goes in the opposite direction — using simple tech, guided by clever ideas, to solve specific problems while embracing **limitations**. For example, if a technology performs better but isn’t readily available, or might discourage a curious DIYer from experimenting, I either avoid it or suggest a more accessible alternative, as long as the alternative can still solve the problem effectively. When I read online that more eco-friendly bioplastics aren’t recommended for outdoor use compared to petroleum-based plastics, I take that as a challenge to find ways to make them work. And more often than not, solutions are there, if you look for them!

Some of the problems tackled here — which also double as stand-alone tutorials — include:

* **Nailing solar power requirements for Raspberry Pi projects.** And yes, solar works even in the UK *if* you meet the right requirements. Blanket statements like “solar doesn’t work in the UK” aren’t helpful. Through field testing (and only field testing), you'll get to what actually works.
* **Scheduling events based on solar time instead of standard clock time.** We used this to capture the dawn chorus of birds, but the same script can automate anything from turning on a terrarium light at sunrise to watering plants at sunset.
* **Updating and checking your remote Raspberry Pi with a 4g Dongle without relying on paid remote access services.**
* **Answering the question: can you trust 3D printed PLA parts for outdoor use?** Spoiler alert: the answer isn’t “no.”
* **Assessing the performance of ultra-cheap MEMS microphones as an alternative to electret mics in DIY projects where audio quality matters.** MEMS connect directly to the Raspberry Pi GPIO and don’t require a separate audio interface.

## Contents

- [Features](#features)
- [Acknowledgements and Origins](#acknowledgements-and-origins)
- [Shopping List](#shopping-list)
- [Wiring](#wiring)
- [3d Printed Parts](#3d-printed-parts)
- [Notes about the Microphones](#notes-about-the-microphones)
- [Overview of the Code Architecture](#overview-of-the-code-architecture)
- [The Safety Measures](#the-safety-measures)
- [How to Control the RPi from Your Home with a 4G Dongle — A real HACK!](#how-to-control-the-rpi-from-your-home-with-a-4g-dongle--a-real-hack)
- [Automating tasks at astral time — Birds don’t sing at office hours...](#solar-crontab--birds-dont-sing-at-office-hours)
- [The Simplest Battery Sensor: ADS1115 breakout with voltage divider](#the-simplest-battery-sensor-ads1115-breakout-with-voltage-divider)
- [Getting The Solar Panel Setup Right](#getting-the-solar-panel-setup-right)

## Features

The streamer has the following features:

* Streams 24/7 stereo audio over the Internet
* Can automate recordings based on solar times (birds don't wear watches!)
* Built with DIYers in mind: Raspberry Pi, open-source code, 3D printing, and affordable, accessible materials
* Small and portable
* Stable and weather-resistant — it can run for months in harsh environments with no maintenance
* Uses the most eco-friendly materials we could reasonably find
* Fully solar-powered
* Remote monitoring and troubleshooting via 4G dongle (includes software updates, shell access, etc.)
* Local access via smartphone hotspot
* Range of audio qualities — suitable for curious DIYers looking for budget solutions, or audiophiles working with dedicated interfaces.

Everything shared here has been field-tested. Our streamers have worked for months, running on solar power even during UK winters, withstanding rain and snow. In their final version, they required minimal maintenance — and I'd say almost none if it weren’t for Storm Darragh, which briefly turned the solar panel into a sail before we tied everything to heavy logs...

---

## Acknowledgements and Origins

Thanks to George Xenakis and Michael Bell from Forest Research for their practical, experience-based suggestions, which consistently proved accurate and saved us a great deal of trial and error. Thanks to Danielle, Max, and Jack at Forestry England for guiding us through the forest and supporting us at every step of the deployment.

Also, huge credit to the amazing [Locusonus project](https://locusonus.org/vitae/index.php?page=Locustream.en) (active since 2006), and their [streambox tutorial](https://locusonus.org/streambox/) — both of which were invaluable starting points.

That said, our 2024 project had different needs, and in the end, it evolved significantly from the original. Here's how it differs:

### Key Differences from the Streambox

* Uses standard Raspberry Pi OS instead of Arch Linux
* No need to give remote access to anyone
* No pre-built OS image: we use a modular approach based on the latest RPi OS + online installers
* Built-in safety checks for remote deployment — automatic issue resolution
* New features:

  * Solar time-based automation
  * Remote code updates and shell access via 4G dongle

---

## Before you start

Make sure you understand the risks of leaving a 12V battery unattended in the field. I’ll repeat it throughout, but it’s worth saying clearly up front:
**Always use a fuse like shown in the wiring section, and thoroughly test your enclosure under both water and direct sunlight.**

**Don’t assume that in 2025 all remote areas have reliable network coverage.**
Alice Holt is a great example. Even in a well-visited, family-friendly forest managed by Forestry England, Anna and I spent a lot of time walking around with SIM cards from four different providers — and still found surprisingly few spots where even one offered a solid signal for our streamer to work.

---

## Shopping list

#### Core Components

* [ ] Raspberry Pi Zero 2W
* [ ] Micro SD card (any size, we used 256GB but calculate storage needs based on recording time)
* [ ] 2 x Windshield (this 3D-printed holder fits the shield for Shure SM57 and mics with similar diameter)
* [ ] **Stereo Audio Input Options we tested**:

  * [ ] 2 × MEMS microphones with breakout (no audio interface needed, extremely cheap but low quality)
    **OR**
  * [ ] RØDE AI-Micro + 2 × Lavalier GO (or other lavalier mics)

#### Solar Power Setup

* [ ] Weather-resistant enclosure (we used a 24-litre Strata storage box made of recycled plastic)
* [ ] Battery Charge Controller with 5V USB Output
* [ ] 5A Fuse
* [ ] Fuse case

* [ ] Winter (December–January)
  * [ ] 4 × 120W solar panels (we used Eco-Worthy)
  * [ ] 120Ah 12V caravan battery

* [ ] Autumn & Spring
  * [ ] 2 × 120W solar panels
  * [ ] Any standard 12V car battery

* [ ] Summer
  * [ ] 1 × 100W solar panel
  * [ ] 7Ah 12V battery

> **Note**: These configurations worked for our specific conditions, and they are on the safe side. Solar requirements vary enormously based on region, sunlight exposure, and shading. For detailed explanation, refer to the relevant section in the guide.

#### Streaming Without LAN

* [ ] 4G USB modem
* [ ] Data SIM card with a suitable monthly plan
* [ ] Audio streaming host (we used StreamUp, supports up to 320 kbps OGG/VORBIS)

#### Battery Monitoring (Optional but very useful to nail the solar power requirements)

* [ ] ADS1115 breakout board
* [ ] 1 × 100kΩ resistor
* [ ] 1 × 330kΩ resistor
* [ ] Small stripboard (with vertical layout preferred)

#### 3D-Printed Case (Optional)

* [ ] 3D printer (to print from our shared model files)
* [ ] 4mm decorative aluminium wire
* [ ] Micro USB input breakout
* [ ] 12mm round waterproof on/off switch
* [ ] 5 × #2 self-tapping pan head 5mm screws
* [ ] 4 × #4 self-tapping pan head 5mm screws
* [ ] 3 × M3 square nuts
* [ ] 3 × M3 pan head 10mm bolts

**The total cost of the shopping list will mostly depend on your online shopping skills!** The most expensive part of the setup is usually the solar panel system, especially if you want the streamer to run 24/7 during winter. The total cost will be much lower if you only plan to stream during the sunnier seasons. For reference, if your goal is year-round streaming with no battery swap, an EcoWorthy 390W + controller package is currently about £200 (we used 4 × 120W panels for extra safety, but 390W should be enough even in the toughest winter months), and a 120Ah campervan lead-acid battery costs a little over £100 — though prices change quickly. The same goes for the SIM plan and 4G modem, as both prices and available models fluctuate so often that listing a fixed cost wouldn’t make sense. In short, if you’re setting up a simple home LAN streamer, all you really need is a Raspberry Pi and an audio capture device. See the section on microphones for a £10 stereo solution or a higher-quality option, but keep in mind that most USB audio devices work fine on an RPi Zero 2W, so the choice ultimately depends on your needs. That said, if you want to go all the way with a fully solar-powered streamer, including a year of SIM coverage and decent audio quality, the overall cost will be more substantial.

---
<br>
<br>
<br>

## Wiring

wiring-diagram

The car battery, fuse, and charge controller go inside a box to protect them from the rain. **Always consider whether children are around!** If there’s any chance someone might touch the terminals, the box needs to be locked.

fuse

In the image on the left, you can see how I connected the fuse: it’s the first thing on the positive terminal of the battery. This way, if a short circuit happens anywhere else in the system, the fuse will blow. After the fuse, there’s a handy lever connector to plug and unplug all the parts that need 12V. In our setup, we send the 12V to the charge controller, which converts it to 5V for the USB powering the RPi. We also send the 12V to the voltage divider (or another step-down converter), which steps it down to 3.3V so the battery sensor can read it. (The digital pins expect a voltage between 0 and 3.3V.)

Drill drainage holes at the bottom of the box, just in case something goes very wrong and water gets inside. If the bettery will be out there for a long time, you can cover the terminals with dielectric grease: it will help prevent corrosion and, being waterproof and non-conductive, add another layer of safety.

For the assembly of the actual streamer with the microphones and the battery sensor, see the following sections.<br>
Once the current is stepped down to USB (5V), it’s much less dangerous to people and less critical if you make mistakes, so feel free to try stuff out! Though it can still damage electronics, the risk of injury or fire comes from mishandling the car battery. That said, I probably don’t need to remind you that most cars have flooded-acid batteries under the hood, and hopefully you don’t see many cars spontaneously catching fire… though their engine bays aren’t exactly waterproof either.

<br>
<br>
<br>

## 3D Printed Parts 

#### Downloads
FreeCAD:<br>
[All](../assets/3d-print/streamer-ads1115-rpiVert-10cm.FCStd)<br>

Meshes:<br>
[Case](../assets/3d-print/Case.stl)<br>
[Lid](../assets/3d-print/Lid.stl)<br>
[Cable Locker](../assets/3d-print/CableLocker.stl)<br>
[Mic Holder (for Lavalier)](../assets/3d-print/MicHolder_Lavalier.stl)<br>
[Mic Holder (for MEMS with round breakout)](../assets/3d-print/MicHolder_MEMS.stl)<br>
[Camera Tripod Adapter](../assets/3d-print/CameraTripodAdapter.stl)<br>
[Tree Shelf](../assets/3d-print/TreeShelf.stl)<br>
[Modem Mushroom Case with antenna holes (for dongles with optional antennas)](../assets/3d-print/ModemCase_Mushroom.stl)<br>
[Modem Flat Case (for SIM7600)](../assets/3d-print/Case.stl)

---

<table>
  <tr>
    <td align="center">
      case<br>
      <strong>Case</strong>
    </td>
    <td align="center">
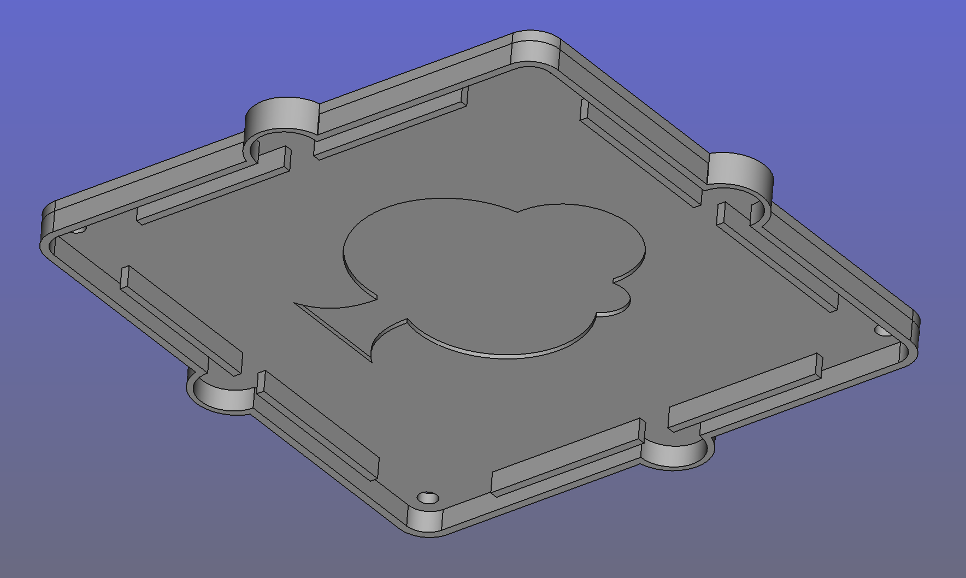
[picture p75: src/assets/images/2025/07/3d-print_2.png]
lid
      <br>
      <strong>Lid (rain hat)</strong>
    </td>
    <td align="center">
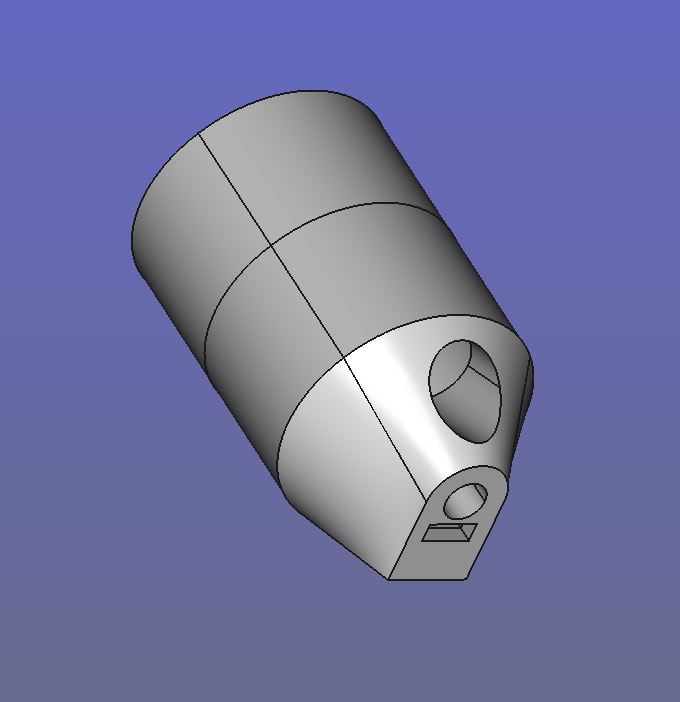
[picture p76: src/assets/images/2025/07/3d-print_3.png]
mic
      <br>
      <strong>Mic holder</strong>
    </td>
  </tr>
</table>

I assembled the parts, starting with the RPi, the battery sensor (see the corresponding section for build instructions), and the waterproof on/off switch. The case measures 10 × 10 × 8 cm, which provides enough space to fit a small USB hub and the AI-Micro.

case

**Note the vertical design for the RPi**. This way, I could collect the recordings by unscrewing only the lid and plugging the SD card directly into a Linux laptop. The root folder can be accessed from the normal file manager, just like an external flash drive. To download 40 GB of recordings, the scp remote protocol won’t help much, unless you can wait hours and hours.

All the parts that need connecting have a rectangular notch where you can slide in an M3 square nut. This holds the machine screw that locks the 4 mm aluminum wire in place. That way, you can move the parts into position, and the 4 mm wire alone is strong enough to keep them steady.
This is useful to control the stereo field of the microphones and the position of the modem - if the modem is too close to the RPi it causes interferences, more on this in the notes about microphones section. In the pictures below, I’m building the mic holder for lavaliers. Its diameter is designed to match the size of windshields for the common Shure SM57, so you can use that as a reference for the fit. 

case

All this parts were printed with standard PLA. And this leads to the question:
Will PLA survive a year of rain and sun in the forest?<br>
The internet: NO!<br>
ChatGPT: NO!<br>
My tests: well...

I didn’t head into the forest with the AI-Micro and the RØDE lavaliers right away. We started our tests with an RPi Zero and a couple of MEMS mics: if it all went horribly wrong, we’d have lost about £20.
A trick to make PLA waterproof and have cute mini boats floating in the bath is using beewax. So I coated the back of the lid with it. I coated the back only to keep the surface of the streamer nice and smooth. On top of that, I added rubber O-rings to the lid screws.

case

I tested it under the shower to make sure the lid design would protect it from water coming from above. It passed.

In the right photo you can see a design detail: the lid has small semicircles with a downward-facing rim. They act like mini-umbrellas for the cable notches, and the rim presses down on the cables so raindrops can’t slide along them into the box (since, well, gravity wants the water to go from top to bottom).

Now, it’s true: PLA isn’t meant for outdoor use — UV light and moisture should eventually wear it down. But… the last version stayed out there from November to August, facing sun, rain, and snow, and not a single drop of water got through the lid. When we finally retired it, it didn’t look too beat up either:

case

So, PLA turns out to be surprisingly resistant.
There are valid concerns about calling bioplastics like PLA eco-friendly—mainly due to how the corn is harvested and the lack of widespread industrial composting facilities—but it does break down much faster than petroleum-based plastics. In the wild, PLA may take around 50 years to decompose, compared to about 500 years for conventional plastics. However, in the right industrial facility, PLA can return to nature in just a few months.
So, while not perfect, there are clear advantages.

---
<br>
<br>
<br>

## Notes about the Microphones

Choosing the right microphone turned out to be quite tricky. Since the equipment would be left unsupervised in a forest, often near a path, starting with high-end gear wasn’t an option.

A common solution online involved using Pi audio HATs with electret microphones, but these HATs tend to go out of production quickly. I wanted something that wouldn’t require rewriting code or adapting to new hardware every few months — so I ruled that out.

**USB microphones** were the next option. Most of the ones I tested were electret-based with onboard ADCs and worked plug-and-play on the Pi (see the first tutorial). But they’re typically mono. Using two with a USB hub might work, but you also need to power a 4G modem from the same hub — all running on battery. More importantly, I wanted flexible mic placement to control the stereo image, and USB mics in their housings make that harder. Bare capsules are easier to mount, protect from rain, and fit into custom 3D-printed enclosures.

**MEMS microphones** offered a lot of advantages:

* No need for an external audio interface or Pi HAT. ADC is onboard the coin-sized breakout.
* Most have 32-bit resolution.
* Extremely low current draw.
* Connect directly to the GPIO.
* Dirt cheap — you can get two (for stereo) for under £5.

For initial tests, especially with an untested DIY waterproof enclosure and uncertain site security, MEMS seemed like the perfect option.

However, their low current draw made them **very sensitive to interference**. 

After solving the interference issues, the quality was acceptable when sounds were relatively loud. But in the forest, silence is common, and at night or during quiet periods, the background noise (digital and noticeable) became an issue.

I then tested a very small audio interface designed for lavalier mics — compact enough to fit in an enclosure meant to go conmfortably up a tree. Few models offer dual input, but the **RØDE AI-Micro** with two **Lavalier GO** mics did the job. The improvement in interference was significant. The modem could sit much closer without problems, and even with the included 1.5 m unbalanced cables coiled up inside the box (right next to the battery wiring!), there was no noticeable interference — surprisingly stable for an unbalanced setup.

Setting up these USB devices is much easier than working with MEMS or Pi HATs. By following the instructions in the README file, you should have them up and running quickly.

> **Note:** The Rode AI-Micro comes — strangely — set to mix the left and right channels into mono by default. If you're using it, make sure to reconfigure it with the provided software, otherwise, you won't get separate left and right channels. This has to be done from a non-Linux machine.

The lavaliers with the AI-Micro is the final audio setup I used to record all the audio files you can hear on Free Sound (link), but only **from March onward**, when I switched from MEMS to the Lavaliers.

---

#### *MEMS michrophones - Gradus ad Parnassum* (or maybe just a slightly less ambitious destination…)

MEMS microphones seem to be here to stay — and they might just become the go-to alternative to the ever-present electret mics for DIY projects. So here’s a bit of experimentation.
No sonograph allowed! Dear DIYer: if I say *“the audio here isn’t good”* but it sounds fine to you, you can skip the suggested improvements.

MEMS posed more problems than advertised.

**Step 1: just make it work.**

For the wiring, there is plenty of info online. [This project](https://makersportal.com/shop/i2s-mems-microphone-for-raspberry-pi-inmp441?srsltid=AfmBOoqB_DKFbKob098QTqIUZ4KEqHDwAs-WXdSmoxllFCNxPV8H_8t5) used exactly the MEMS breakout I found in stereo configuration, and the pins on Raspberry Pi zero 2W are the same.

You'll need to solder the headers and probably have a crimper for the connections. Initially, just use whatever cables you have.

Here’s what a MEMS mic can sound like if you:

* mismatch the bit resolution,
* don’t shield the cables, and
* use cables that are too long.

[▶️ Sound of MEMS with bit mismatch and unshielded cables, mono](https://raw.githubusercontent.com/sensingtheforest/sensingtheforest.github.io/main/src/assets/audio/1_mems_mono_16bit_shield-not-grounded.wav)

Keep in mind that these recordings were made in quiet settings, and the volume is relatively high to make details more audible.
But I promise, I’m not recording a synth with a random LFO — what sounds like a vintage oscillator is pure interference picked up by the unshielded cables in a noisy RF environment! Listening to nighttime forest sounds with this setup would be an unpleasant experience...

**Step 2: let’s get the cable length and shielding right.**

Now you’ll almost certainly need to deal with the shield, and 5-core shielded cables aren’t exactly common. You should be able to find them online, or you can make your own DIY shield.

mems-cables

On the left is a single mic, which I secure to the 3D-printed socket with hot glue. On the right are the two ends of the left and right mics, twisted together and crimped with the same connector. If you’re thinking in terms of analog audio, this might seem counterintuitive, but this is digital. Yes, L and R share some joined cables, yet you’ll still get separate channels on the Raspberry Pi — as long as you solder the R channel control pin to Vdd and the L channel control pin to ground. You can do this directly on the MEMS breakout board by connecting the Vdd pin to the control pin on one microphone, and ground to the control pin on the other.

The bit resolution is still mismatched, but the cables are now shielded — with the shield connected only on the Raspberry Pi side, tied to ground along with the cable ground.

[▶️ Sound of MEMS with bit mismatch and 50cm shielded cables, mono](https://raw.githubusercontent.com/sensingtheforest/sensingtheforest.github.io/main/src/assets/audio/2_mems_mono_16bit_shilded_medium-cable.wav)

The "synth" is quiter but still noticeably there. Cables are probably too long. Let's cut them from 50cm to about 15cm.

[▶️ Sound of MEMS with bit mismatch and 15cm shielded cables, mono](https://raw.githubusercontent.com/sensingtheforest/sensingtheforest.github.io/main/src/assets/audio/3_mems_mono_16bit_shielded_short-cable.wav)

Now, the “synth” is almost gone. Not perfect, but a major improvement. 

>**Note:**  There's no fixed rule for cable length. It depends entirely on the strength of RFI (radio frequency interference) in your environment. If you place the setup near a power line or a strong light source, it might not work at all. But in a low-interference area, a 1-meter cable might be just fine.

**Step 3: Can a bit-depth mismatch really cause that much trouble?**

My bit depth was 16-bit (S16\_LE). That’s wrong for most MEMS mics, which are typically 32-bit (S32\_LE).
This is the relevant part of the ALSA config file (`/etc/asound.conf`) 

```
pcm.mic_hw {
    type hw
    card sndrpii2scard
    channels 2
    format S16_LE   #16-bit is usually wrong for MEMS
}
```

[▶️ Sound of MEMS with bit depth mismatch, shielded and short cables, stereo](https://raw.githubusercontent.com/sensingtheforest/sensingtheforest.github.io/main/src/assets/audio/4_mems_stereo_16bit-instead-of-32_short-cable.wav)

Fixing the bit mismatch in the ALSA config file improved things a lot.

```
pcm.mic_hw {
    type hw
    card sndrpii2scard
    channels 2
    format S32_LE
}
```

[▶️ Sound of MEMS with correct bit depth, shielded and short cables, stereo](https://raw.githubusercontent.com/sensingtheforest/sensingtheforest.github.io/main/src/assets/audio/5_mems_stereo_32-bit-as-intended_short-cable.wav)

These recordings are from a morning in Bristol, and yes, we have a lot of seagulls here.
I expected it to reduce background noise — no surprises there — but it also helped significantly with interference when I moved everything to the forest, which I hadn’t anticipated, at least not to that extent. 

ALSA can be a bit unforgiving. If you don’t know the exact bit format of your device (not just the depth, but the label), it’s a real problem. Unfortunately, to figure it out for sure, you’ll probably need tools that come with PipeWire. That's what I used to discover that the AI-Micro works with 24-bit audio, 3 bytes per sample, Little Endian (S24_3LE). But if you’d rather avoid installing all that, a few educated guesses usually work. Start by trying `S32_LE`, then `S24_LE`.

**Step 4: The mic sounds decent, time to plug in the modem and head to the forest? Not so fast...**

You plug in the modem — and you hear a nasty glitch. You might think the mic’s broken. It’s not. That sound is **modem interference**, especially if you're trying to place it inside the same box as the MEMS mic and audio cables.

[▶️ Sound of MEMS next to the modem, stereo](https://raw.githubusercontent.com/sensingtheforest/sensingtheforest.github.io/main/src/assets/audio/6_mems_mono_16bit_near-modem.wav)

That’s the reason I built a separate modem case, connected by an aluminium wire — to isolate it from the audio path.

Move the modem farther away, and the glitch starts to fade:

[▶️ Sound of MEMS 30cm away from the modem, stereo](https://raw.githubusercontent.com/sensingtheforest/sensingtheforest.github.io/main/src/assets/audio/7_mems_mono_16bit_far-modem.wav)

And with proper shielding and enough distance, we’re back to where we started before plugging in the meodem.

---

**Circuit corrosion is real in the forest**

mems-oxidation

On the left pic, you can see what happened to the exposed circuits after just a few weeks without protection.<br>
On the right, the fix: **applying acrylic conformal coating with a tiny brush solves the issue** — just make sure not to cover the mic hole!

In the rainy season, corrosion progresses faster, but it always starts gradually. Listen to the left channel below: the clicks aren’t rain; compare them to the right channel. This recording was made on September 23.

[▶️ Sound of MEMS with beginnings of corrosion on the L channel](https://raw.githubusercontent.com/sensingtheforest/sensingtheforest.github.io/main/src/assets/audio/8_corrosion-start.wav)

And yes, when advanced corrosion causes full short circuits, it can sound a lot closer to a Merzbow performance than to an idyllic forest soundscape! This is how it sounded on September 27, after four more humid days—volume reduced by 12 dB to spare your ears...

[▶️ Sound of MEMS with advanced corrosion on the L channel](https://raw.githubusercontent.com/sensingtheforest/sensingtheforest.github.io/main/src/assets/audio/9_corrosion-full.wav)

---
<br>
<br>
<br>

## Overview of the Code Architecture

Most of the code is written in Bash, with Python scripts handling more time-sensitive tasks like reading the battery sensor and syncing with solar time.
System functions and global variables are defined in the `common.sh` script. <br>
**`common.sh` also acts as the main user configuration file. Many parameters of the streamer can be adjusted there, and each option is commented directly in the file.**

For audio streaming, I used Darkice, like Locusonus and many other similar projects online.

For full details, the code is available in our [GitHub repository](#), and it's (hopefully!) well-commented. But here's a quick overview of the core structure of the streaming component:

```bash
boot.sh -> opens a detached screen session that runs stream.sh
   └── stream.sh -> runs monitor_stream() (a main while loop)
         └── monitor_stream() -> checks if darkice is running
               └── If not, starts darkice via start_darkice()
```

#### Monitoring Strategy

Instead of a simple `ps aux | grep darkice` process check (which often fails in edge cases), I implemented **live terminal parsing** of Darkice's output:

* If output ends with `SCHED_FIFO` → everything is fine, set streamer state to `1`
* If keywords like `reconnecting  0` or `TcpSocket` appear → set state to `0`, even if it later recovers (more about this later)

This state is stored in the `state.txt` file and read regularly to assess streaming health.

#### Why Live Parsing?

During field testing, I noticed Darkice could remain an active process but **fail silently** — e.g., not actually streaming due to a network dropout or crash. Live output parsing fixed that.

Now, if Darkice hits a known error state, it's killed and restarted. This even helps revive the remote streaming server — in our case StreamUp – likely because restarting triggers a fresh connection that resets the server-side socket state.

> **Note:** This method depends on specific terminal outputs from Darkice (set using `verbosity=6`). If future Darkice versions change these messages, the function will need to be updated.

---

#### Persistent Execution

* The main loop (`monitor_stream`) runs inside a **detached screen session** so it can operate independently of SSH connections.
* `boot.sh` sets everything in motion by launching the screen session at system startup using a **systemd** service.

See [**Tutorial One**](https://sensingtheforest.github.io/2024/01/17/phase-1-setting-up-the-streamers/) for more details on `screen`.

---
<br>
<br>
<br>

## The Safety Measures

If you plan to leave the Streamer in a remote area, these are really (but REALLY) important. In the forest, literally everything that *could* go wrong, *did* go wrong. So here we tackle the software side of surviving the wilderness. Sure, if a tree falls on the Streamer, software won’t save you—but for many other adversities, we have error routines.

There are four levels of checks.

---

#### Level 1: `start_darkice()`

```bash
start_darkice() {
    if status_darkice; then
        log "start_darkice() - Darkice already running -> Kill and restart"
        kill_darkice
    fi
    log "start_darkice() - Start darkice with real-time output line check"
    sudo darkice -c "$PROJECT_FOLDER/darkice.cfg" -v 6 | while IFS= read -r darkice_line; do
        echo "$darkice_line" | tee -a "$LOG_FILE"
        if [[ "$darkice_line" == *"reconnecting  0"* || "$darkice_line" == *"TcpSocket"* || "$darkice_line" == *"No such device"* ]]; then
            set_darkice_state 0
        elif [[ "$darkice_line" == *"SCHED_FIFO"* ]]; then
            set_darkice_state 1
        fi
        sleep 0.1
    done
}
```

This function in `common.sh` watches Darkice’s terminal output in real time and flags issues we learned the hard way after a year of forest deployment. Around 80% of those issues were internet-related.

* `'reconnecting  0'` and `'TcpSocket'` usually meant the modem or network coverage had a meltdown.
* `'No such device'` was a fun one—it appeared when the AIMicro or Rode lav mic just decided not to exist anymore (after *months* of working fine, of course). It turned out the issue was failing USB cables or connections, which caused power shortages to the USB peripherals. Obviously, I didn’t get a simple on/off failure — that would’ve been easier to deal with. Instead, I had to troubleshoot increasingly intermittent and unreliable behaviour...

This function only **flags** problems. The actual fixing comes in later steps.

---

#### Level 2: `monitor_stream()`

This function runs every `DARKICE_MONITOR_INTERVAL` seconds (default: 60 — tweak it in `common.sh`). It checks the Darkice streaming state stored in `state.txt`.

If the flag is 0, it restarts Darkice. This solved a really annoying issue: when Darkice froze, sometimes the streaming server froze too. So even after Darkice came back, the server stayed unresponsive until we manually restarted it via CentovaCast.

Magically, restarting Darkice in these situations solved the server issue. Why? No idea. Maybe it reset the transmission protocol. Maybe it was just scared of getting rebooted again. But it worked.

---

#### Level 3: `monitor.sh`

This script is triggered by `crontab` every hour and takes a more “surgical” approach to problem-solving.

**Summary of what it does:**

* Checks if the Raspberry Pi has internet access.
* If not:

  * If using a dongle (not Wi-Fi), check and refresh the dongle's IP. If still down, reboot the dongle.
  * If using Wi-Fi, try reconnecting to known networks.
* If the internet comes back, restart the streaming session.
* Then verify if Darkice is *really* streaming (not just running). If stuck, kill the stream session and restart it.
* If recording is enabled, make sure `solar-crontab.py` is running. If not, restart it in a `screen` session.

---

#### Level 4: `nuclear-option.sh`

A bit of a dramatic name for a script that *just reboots the system*. But hey, when you're 5 hours away and stuck without logs, dramatic works.

Working in the forest was lovely—coding on a fallen tree while birds chirped around me—but driving back and forth every time the Pi decided to sulk wasn’t ideal.

The nuclear option was designed for those moments when nothing else works—especially if the modem crashes or your mobile provider surprises you with an unexpected IP change. The Raspberry Pi doesn’t always handle these disruptions gracefully, and sometimes a reboot is the only way to recover. Even before proper fallback routines kick in, a simple reboot can buy you another 12 hours of IP lease. And those 12 hours might be all you need to regain remote access and fix the issue.

In my case, those extra 12 hours after each reboot gave me time to remotely assign a permanent IP address to the modem, solving the lease expiry problem, thus sparing me a trip to the site, and, most importantly, avoiding any loss of recordings.

I set up this script to run once a day at 3 AM. Since rebooting sends logs via email and could cause more things to go wrong than the monitor script, I keep it rare.

---
<br>
<br>
<br>

## How to Control the RPi from Your Home with a 4G Dongle — A real HACK!

When I finally got the 4G dongles to work, it sounded great... until I realized I couldn’t just SSH into the Raspberry Pi sitting deep in the woods. These dongles with SIM cards basically act like smartphones — and you wouldn’t want people SSH-ing into your phone either, right? Carriers make sure of that by throwing in things like CGNAT and constantly changing public IPs. Great for security, terrible for remote hacking (uh, I mean *maintenance*).

Sure, you could pay for services that give you a stable IP and remote access — just like they do for security cams — but where’s the fun in that? Hacks are free, fun, and they add that touch of cyberpunk.

---

#### Wait... Viruses Do This All the Time!

The idea is simple. Viruses often work by getting you to download a sketchy file that runs code on your machine. What if *we* are both the sender *and* the receiver — and we actually *trust* our code? Congratulations, you just reinvented the concept of **automatic updates**.

In a few words: we have a shared space (like an email inbox), the RPi checks it regularly, and if it finds something shiny (aka an email with a subject of your choice and with an attachment), it downloads and runs it.

---

#### The Simplest Possible Shared Repo: Email

Yes. Email. Literally Gmail.

To set this up:

* Enable IMAP on your Gmail account
* Write a Python script that checks for emails with a specific subject and grabs the attachments
* Tell the Pi to run that script on a schedule and execute the goodies it downloads

#### How to Enable IMAP on Gmail

1. Open Gmail, click the gear icon (top-right), then “See all settings”
2. Go to **Forwarding and POP/IMAP**
3. Under **IMAP Access**, select “Enable IMAP”, then click “Save Changes”

Done.

---

#### The Python Snippet That Does the Job

This little script checks your Gmail inbox, looks for emails with a certain subject from the past few days (tweak this with the var SEARCH_DAYS), and downloads any attachments into your Pi's project folder.
**Heads up:** Don’t forget to enable IMAP on your email and update the placeholders in the Email account credentials section of the code before running it!

```python
from pathlib import Path
import imaplib
import email
import os
from datetime import datetime, timedelta

# --- Email account credentials and script config (edit this section!) ---
IMAP_SERVER = "imap.gmail.com"
EMAIL_ACCOUNT = "your-email@gmail.com"
PASSWORD = "your-app-password"  # Use a Google app password, not your main account password
PROJECT_DIR = Path(__file__).resolve().parent
SEARCH_SUBJECT = "update code myProjectName"  # <-- Change to match your subject line
SEARCH_DAYS = 3  # Number of days to look back in the inbox
# ------------------------------------------------------------------------

print("______________UPDATE CODE")

# Calculate the date x days ago in IMAP format (DD-MM-YYYY)
date_x_days_ago = (datetime.now() - timedelta(days=SEARCH_DAYS)).strftime("%d-%b-%Y")

# Connect to email server
mail = imaplib.IMAP4_SSL(IMAP_SERVER)
mail.login(EMAIL_ACCOUNT, PASSWORD)
mail.select("inbox")

# Search for emails with the subject and date filter
search_criteria = f'(SINCE {date_x_days_ago} SUBJECT "{SEARCH_SUBJECT}")'
status, messages = mail.search(None, search_criteria)

email_ids = messages[0].split()
if not email_ids:
    print(f"No recent emails found with subject: {SEARCH_SUBJECT}")
else:
    latest_email_id = email_ids[-1]
    status, data = mail.fetch(latest_email_id, "(RFC822)")
    msg = email.message_from_bytes(data[0][1])

    print(f"From: {msg['From']}")
    print(f"Subject: {msg['Subject']}")
    print(f"Date: {msg['Date']}")

    # Loop through email parts to find attachments
    for part in msg.walk():
        if part.get_content_disposition() == "attachment":
            filename = part.get_filename()
            if filename:
                filepath = os.path.join(PROJECT_DIR, filename)
                with open(filepath, "wb") as f:
                    f.write(part.get_payload(decode=True))
                print(f"Saved attachment: {filepath}")

mail.logout()
print("DONE")
```

---

#### What If You Just Want to Run Shell Commands?

Great question. You’re not always uploading new scripts — sometimes you just want to run a `reboot`, or log the CPU temp, or sacrifice a process to the gods of uptime.

Here’s the plan: we download a shell script via email (same method as above), and run it if it exists. Since we’ve already automated the email checking, we don’t want to repeat the commands every time the cronjob kicks in.

So, here comes the little extra step that makes it all neat and modular.

This helper script `blank.sh` looks for a file called `commands-tray.sh` in the project folder — a sort of “meal tray” you send via email. It contains all the commands you want the RPi to execute.

The moment we run `blank.sh` and it finds a file called `commands-tray.sh` with the bash commands, it eagerly devours its contents (i.e., runs the commands), logs the output, and then throws the tray in the bin (i.e., deletes `commands-tray.sh`) so it doesn’t rerun the same stuff over and over—unless you forget to delete the email, in which case it will keep finding commands to execute.

```bash
source "$(dirname "$(realpath "${BASH_SOURCE[0]}")")"/common.sh
script_name=$(basename "${BASH_SOURCE[0]}")

commands_script="$PROJECT_FOLDER/commands-tray.sh"
temp_log=$(mktemp)

if [[ -f "$commands_script" && -s "$commands_script" ]]; then
    log "$script_name - Executing $commands_script..."
    log "$(cat $commands_script)"
    source "$commands_script" > >(tee -a "$temp_log") 2>&1
    log "$(cat "$temp_log")"
    log "$script_name - Execution completed. Deleting $commands_script..."
    sudo rm -f "$commands_script" && rm -f "$temp_log"
else
    log "$script_name - No commands to execute."
fi

if [[ -n "$reboot" && "$reboot" -eq 1 ]]; then
    log "$script_name - Rebooting now..."
    sudo reboot
fi
```

---

#### Automate blank.sh With Cron

We want the RPi to check its inbox regularly, so we set up a cronjob to download the attachments and run balnk.sh a few seconds after:

```md
0 * * * * $HOME/audio-streamer/venv/bin/python $HOME/audio-streamer/update-code.py && sleep 10 && $HOME/audio-streamer/blank.sh
```

This runs every hour. If you're confident everything’s stable, once a day should be fine too.

---

That’s it. You’ve now got remote, wireless, email-powered code deployment and shell control for your Raspberry Pi in the middle of nowhere — no subscriptions, no exposed SSH ports, no nonsense. Just some hackery.

---

#### Remote Command Greatest Hits (Only the Ones That Actually Worked)

Here’s a little greatest hits mixtape of the remote commands I sent to the streamer by uploading `commands-tray.sh`. Only the ones that *actually did something useful* made it into this list.

> Reminder: `blank.sh` uses `source` to load `commands-tray.sh` (not a subshell), so all the global variables from `common.sh` are available in the current session.

- **Reboot**

This is the **only command with special syntax** because it gets executed **after** the script finishes.
**Don't** use `sudo reboot` here — otherwise, the script will halt before cleaning up temporary files or deleting itself.

```bash
reboot=1
```

From here on, just standard bash...

- **Send the Latest System Log**

You'll receive `sys.log` in your inbox the next time `blank.sh` runs.

```bash
$PROJECT_FOLDER/send-email.sh
```

- **Get the Current Configuration Files of the Streamer**

Send the key config files one by one.

```bash
$PROJECT_FOLDER/send-email.sh -a $PROJECT_FOLDER/darkice.cfg -s "STREAMER CONFIG: darkice.cfg"
$PROJECT_FOLDER/send-email.sh -a $PROJECT_FOLDER/update-code.py -s "STREAMER CONFIG: update-code.py"
$PROJECT_FOLDER/send-email.sh -a $PROJECT_FOLDER/solar-crontab.py -s "STREAMER CONFIG: solar-crontab.py"
$PROJECT_FOLDER/send-email.sh -a $PROJECT_FOLDER/common.sh -s "STREAMER CONFIG: common.sh"
$PROJECT_FOLDER/send-email.sh -a ~/.msmtprc -s "STREAMER CONFIG: msmtprc"
```

Or just send them all in one email — `send-email.sh` accepts multiple attachments.

```bash
$PROJECT_FOLDER/send-email.sh \
  -a $PROJECT_FOLDER/darkice.cfg \
  -a $PROJECT_FOLDER/common.sh \
  -a $PROJECT_FOLDER/update-code.py \
  -a $PROJECT_FOLDER/solar-crontab.py \
  -a ~/.msmtprc \
  -s "STREAMER CONFIG: Full config dump"
```

- **Update cronjobs**
  
Replace specific lines in your crontab with new ones.

Edit the remote update check to run every hour (at minute 20),
instead of every 4 hours as defined in the default cronjob.

```bash
crontab -l | sed 's|0 \*/4 \* \* \* \$HOME/audio-streamer/venv/bin/python \$HOME/audio-streamer/update-code.py|20 * * * * $HOME/audio-streamer/venv/bin/python $HOME/audio-streamer/update-code.py|' | crontab -
```

- **Amend a cronjob to use a new script**
```bash
crontab -l | sed 's|\$HOME/audio-streamer/email-log.sh|\$HOME/audio-streamer/send-email.sh|' | crontab -
```

- **Save your crontab contents to sys.log and send it**
```bash
crontab -l >> "$PROJECT_FOLDER/sys.log"
$PROJECT_FOLDER/send-email.sh
```

- **Log all audio files and email the list**
```bash
ls -1 "$PROJECT_FOLDER/audio" > "$PROJECT_FOLDER/rec.log"
$PROJECT_FOLDER/send-email.sh -a $PROJECT_FOLDER/rec.log -s "STREAMER DATA: Audio recordings log"
```

- **Uploaded a sys file and it's not working? Often, a just matter of permissions**
  
Check the sys.log for clues: it usually shows a "permission denied" error. To solve this, grant read permission (+r) to all users (a) to fix it and try sending it again via email:
```bash
sudo chmod a+r /etc/asound.conf
$PROJECT_FOLDER/send-email.sh -a /etc/asound.conf -s "STREAMER SOUNDSCAPE: Current asound.conf"
```

---
<br>
<br>
<br>

## Solar Crontab — *Birds don’t sing at office hours!*

The usual way to schedule things on Linux is with good old `crontab`. You pick an hour, a day, a month, and the job gets done. But nature doesn’t run on clocks — it runs on light.

When we set up our forest recorder, we really wanted to capture dawn choruses of the birds that starts just before sunrise and fades as the day begins. So syncing with the sun was a must.

That's where this script comes in: it triggers scripts or Python functions **based on solar events**, not man-made time. It's flexible too — I've used it to turn on terrarium lights, water a garden, and yes, start a remote recording session as soon as the birds start gossiping.

This version is cleaned up and doesn't depend on the audio streamer repo, so you can use it for any project.

---

#### How it works

* You define a **location** (lat/lon + timezone).
* You specify some **solar ratios**:
  `0` = sunrise, `1` = solar noon, `2` = sunset.
  You can get creative — e.g., `2.5` is halfway between sunset and the *next* sunrise (i.e., middle of the night).
* You assign a **command** (bash script or Python function) to each ratio.
* The script checks the solar events for *today*, waits until the next one, runs the command, and repeats forever like a tiny sun-worshipping daemon.

---

#### Python script and setup

```python
from pathlib import Path
import os
from datetime import datetime, timedelta
import time
import zoneinfo
from astral import LocationInfo
from astral.sun import sun

#################################################
# Edit your parameters here:

location = LocationInfo("Alice Holt Forest", "UK", "Europe/London", 51.1699307, -0.8371404)

# Solar ratios: 0 = sunrise, 1 = noon, 2 = sunset, 2.5 = night (between sunset and sunrise)
solar_ratios = [0.0, 1.0, 2.0, 2.5]

SCRIPT_DIR = Path(__file__).resolve().parent
commands = [""] * len(solar_ratios)

# Shell scripts or Python functions
commands[0] = os.path.join(SCRIPT_DIR, "record.sh")
commands[1] = os.path.join(SCRIPT_DIR, "record.sh")
commands[2] = os.path.join(SCRIPT_DIR, "record.sh")
commands[3] = os.path.join(SCRIPT_DIR, "record.sh")

# If you need to use Python functions instead of shell scripts,
# assign them without parentheses or arguments. You can mix bash and Python functions.
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

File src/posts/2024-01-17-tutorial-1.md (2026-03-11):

---
title: Phase 1 - Setting up the streamers
date: 2024-01-17T10:00:00.000Z
excerpt: In this introductory tutorial, I will walk you through the basic steps to get started with audio streaming on your local LAN.
permalink: /streamers/tutorial-1/
author: luigi-marino
draft:
seo:
  title:
  description:
  image: 2024/01/tutorial1_pic1.jpg
images: # relative to /src/assets/images/
  feature: 2024/01/tutorial1_pic1.jpg
  thumb: 2024/01/tutorial1_pic1.jpg
  align: # object-center (default) - other options at https://tailwindcss.com/docs/object-position
  height: h-auto # optional. Default = h-48 md:h-1/3
tags:
  - acoustic-ecology
  - development
  - diy-streamer
  - do-it-yourself  
  - locus-sonus
  - raspberry-pi
  - soundscapes
  - streamers
  - tutorials
---

We want to create audio streamers to broadcast the sounds of the forest remotely on the Internet of Things (IoT). In this way, we can share the audio feed with a community of creatives and scientists for music, installations, collecting data about the state of the forest, and hopefully other applications that will come up along the way.

Ideally, our streamers should be:
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

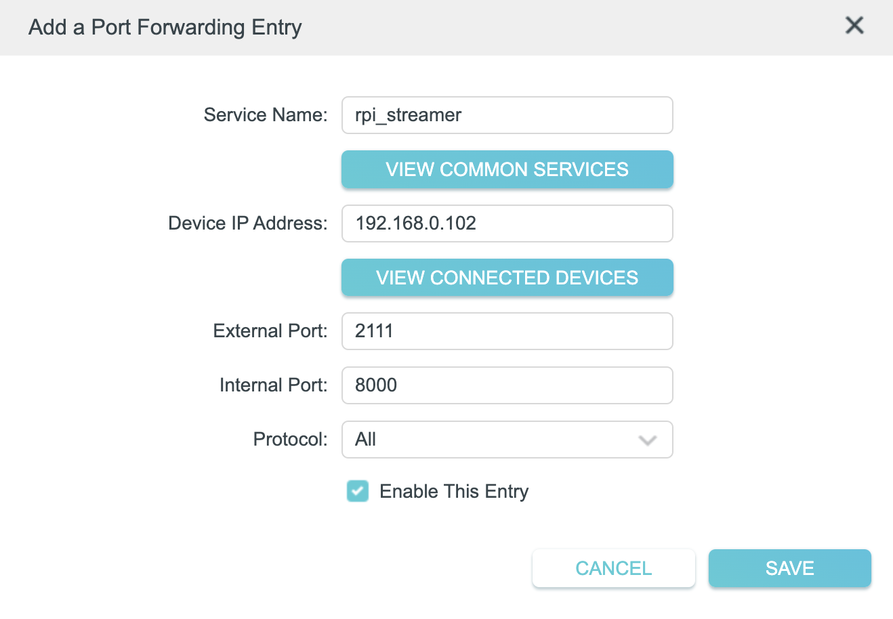
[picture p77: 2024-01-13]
src/assets/images/2024/01/tutorial1_pic4.png

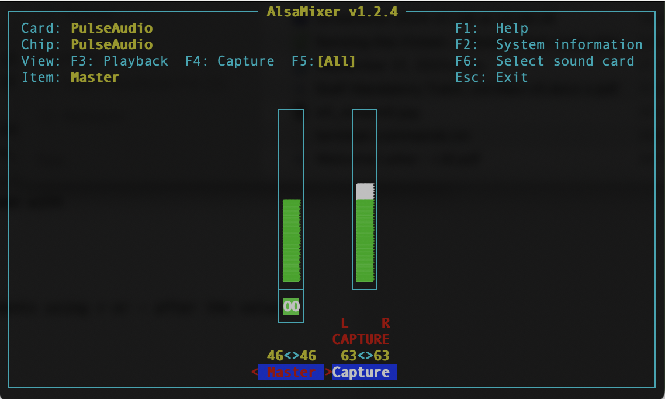
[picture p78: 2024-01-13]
src/assets/images/2024/01/tutorial1_pic3.png

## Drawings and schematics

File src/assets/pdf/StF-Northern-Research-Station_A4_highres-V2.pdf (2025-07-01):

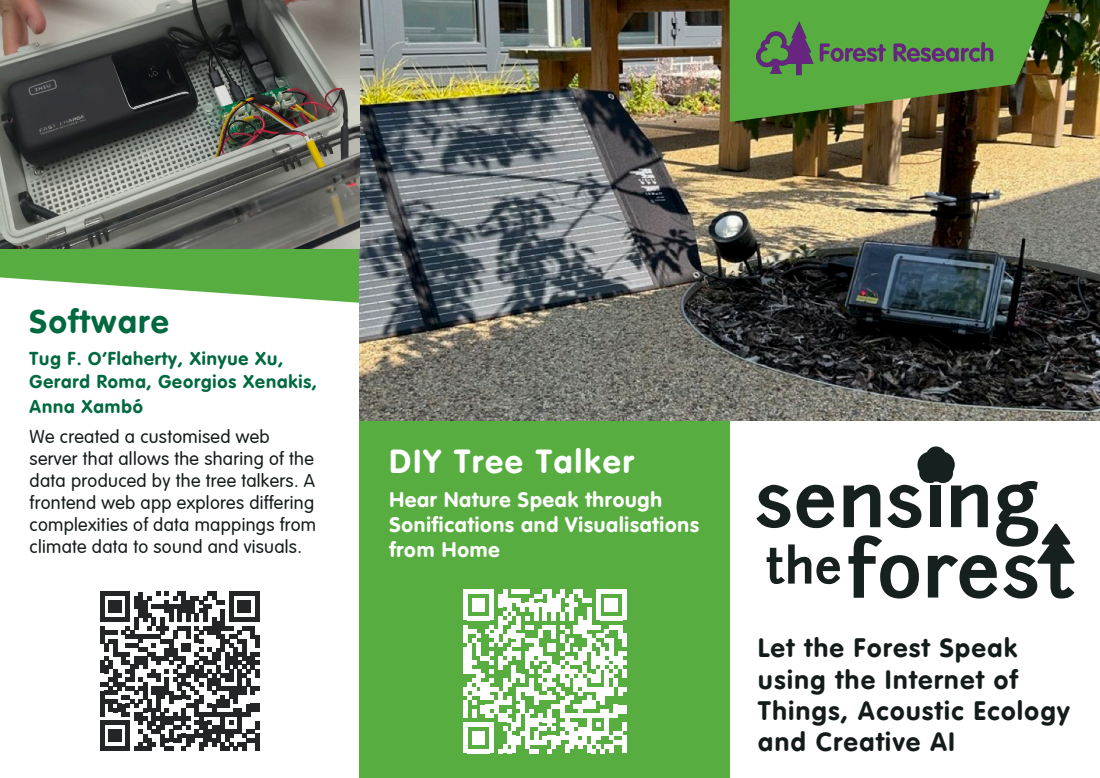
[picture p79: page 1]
Software

Tug F. O’Flaherty, Xinyue Xu,
Gerard Roma, Georgios Xenakis,
Anna Xambó
We created a customised web
server that allows the sharing of the
data produced by the tree talkers. A
frontend web app explores differing
complexities of data mappings from
climate data to sound and visuals.

DIY Tree Talker
Hear Nature Speak through
Sonifications and Visualisations
from Home

Let the Forest Speak
using the Internet of
Things, Acoustic Ecology
and Creative AI

## Sensing the Forest at the Northern

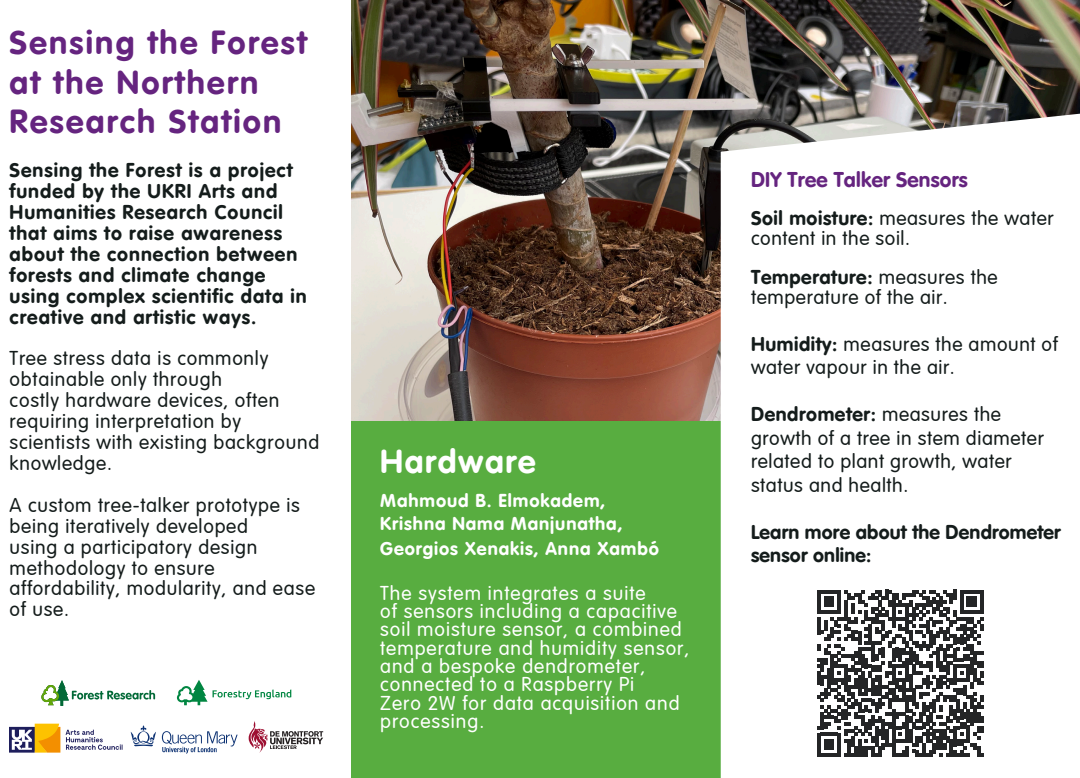
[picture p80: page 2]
Research Station; Hardware

Sensing the Forest is a project
funded by the UKRI Arts and
Humanities Research Council
that aims to raise awareness
about the connection between
forests and climate change
using complex scientific data in
creative and artistic ways.
Tree stress data is commonly
obtainable only through
costly hardware devices, often
requiring interpretation by
scientists with existing background
knowledge.
A custom tree-talker prototype is
being iteratively developed
using a participatory design
methodology to ensure
affordability, modularity, and ease
of use.

DIY Tree Talker Sensors
Soil moisture: measures the water
content in the soil.
Temperature: measures the
temperature of the air.

Humidity: measures the amount of
water vapour in the air.

Dendrometer: measures the
growth of a tree in stem diameter
related to plant growth, water
status and health.

Mahmoud B. Elmokadem,
Krishna Nama Manjunatha,
Georgios Xenakis, Anna Xambó
The system integrates a suite
of sensors including a capacitive
soil moisture sensor, a combined
temperature and humidity sensor,
and a bespoke dendrometer,
connected to a Raspberry Pi
Zero 2W for data acquisition and
processing.

Learn more about the Dendrometer
sensor online:

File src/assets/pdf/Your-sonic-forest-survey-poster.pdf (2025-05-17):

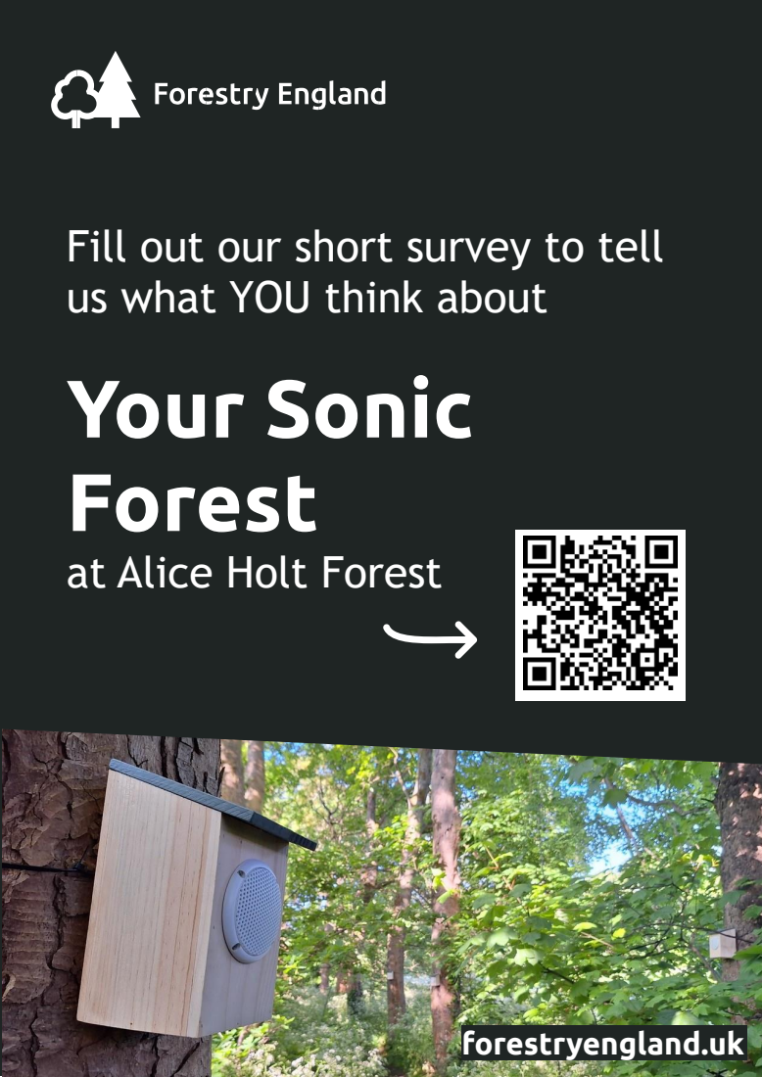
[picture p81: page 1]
forestryengland.uk

Fill out our short survey to tell
us what YOU think about
Your Sonic
Forest

at Alice Holt Forest
